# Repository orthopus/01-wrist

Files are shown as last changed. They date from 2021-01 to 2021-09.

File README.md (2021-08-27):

# Universal wrist & Tool holder

This repository contents documentation of : 

- ➡ **The Universal Wrist** : a mechanical wrist and his mechanical tool-holder. Adapted to upper-limb amputations including disarticulation of the  wrist, this mechanical wrist fits directly into a socket and connects quickly to a large number of terminal devices such as the [ORTHOPUS Work Hook or the Aesthetic Hand](https://orthopus.com/en/upper-limb-prosthetics/). *You can find [buying informations on this page](https://orthopus.com/en/universal-wrist/).*

  
  

- ➡ **The Tool holder** : compatible with the ORTHOPUS Universal Wrist. You can already find a 3D printed version, compatible with [mechanicals tools for upper limb amputees](https://github.com/orthopus/01-mechanicals-tools). *Scroll below to see the tool holder's documentation.*
  
  

>#### WARNING NOTICE BEFORE STARTING
>The Do It Yourself (DIY) versions of our solutions are not CE marked. CE marking is only applicable to solutions developed and sold by ORTHOPUS because their design follows the current regulations. ORTHOPUS cannot guarantee the “quality” of solutions replicated by third parties thanks to the documentation shared on github.

## UNIVERSAL WRIST

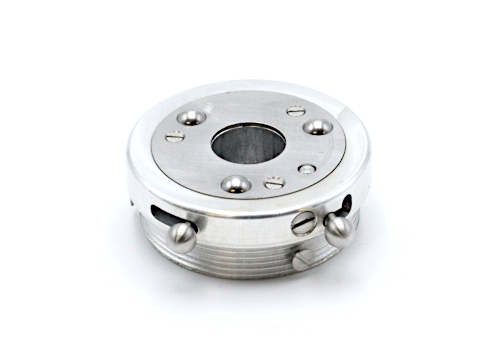
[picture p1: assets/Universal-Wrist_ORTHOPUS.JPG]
UniversalWrist_ORTHOPUS


#### HOW TO MAKE YOUR OWN UNIVERSAL WRIST

***D.I.Y difficulty level :* ⭐⭐⭐⭐⭐**

To make your own Universal Wrist, you will need advanced workshop machinery and some basics components. You can find a detailed list of equipment and the steps to follow in the **[UNIVERSAL WRIST MAKING MANUAL](./docs/wrist/UniversalWrist_making-manual.md)**)

The Bill of Material shown below is downloadable with clickable links [here](https://github.com/orthopus/01-wrist/blob/main/src/Wrist/ILL-0109-BoMGitHub.pdf) details standard components as well as parts that need to be machined.

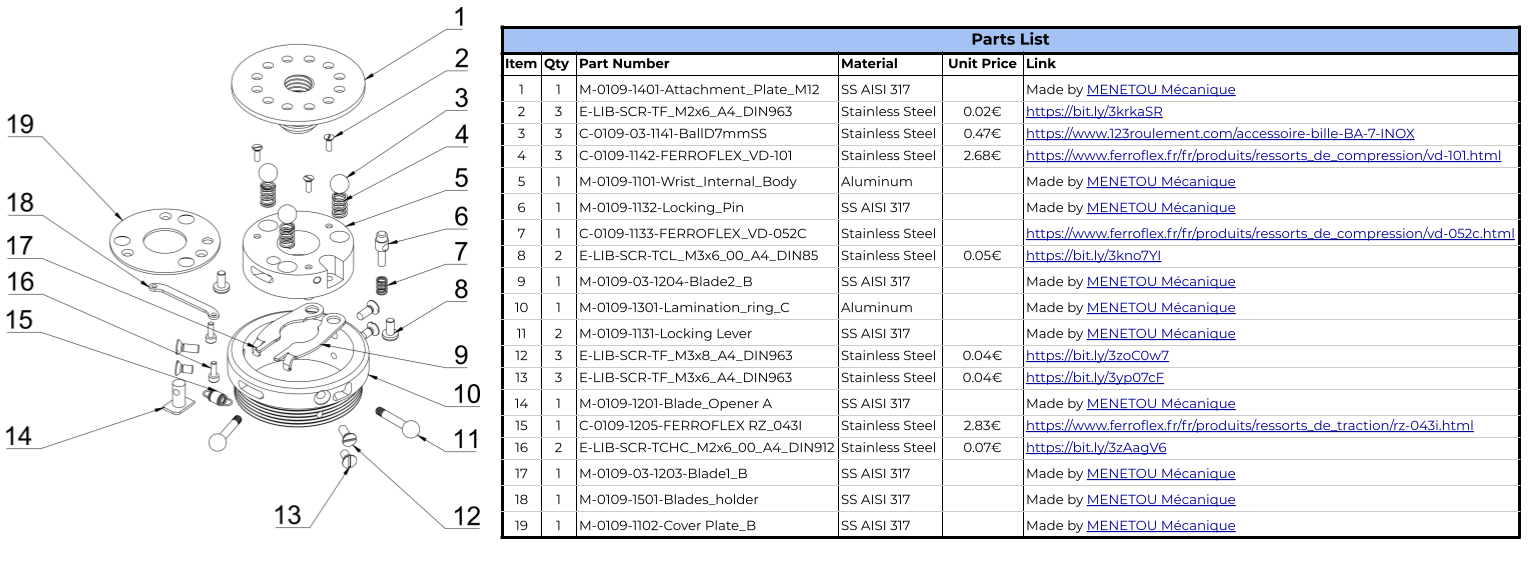
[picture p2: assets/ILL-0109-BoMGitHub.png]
ILL-0109-BomGithub


To get the best experiences with the **Universal Wrist**, full product details are provided in the [INSTRUCTIONS FOR USE](https://orthopus.com/wp-content/uploads/2021/06/IFU-OR-0109-Universal-Wrist-ORTHOPUS-Instructions-For-Use.pdf).

## TOOL HOLDER 3D PRINTED

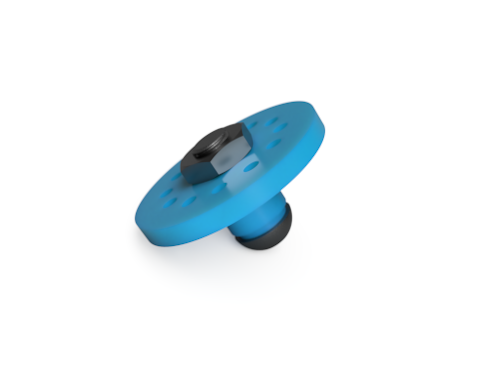
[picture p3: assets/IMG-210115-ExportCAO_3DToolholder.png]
IMG-210115-ExportCAO_3DToolholder


#### HOW TO MAKE YOUR OWN  TOOL HOLDER 3D PRINTED

***D.I.Y difficulty level :* ⭐⭐**

To make your own Tool Holder, you will need a 3D printer, a grinder machine or a metal file, and some basics screws. You can find a detailed list of equipment and the steps to follow in the **[TOOL HOLDER 3D PRINTED MAKING MANUAL](./docs/tool-holder-3D-printer/ToolHolder_3D_making-manual.md)**

You can make the Tool holder for less than 1€ : more details in the Bill of Material shown below and available with clickable links [here](https://github.com/orthopus/01-wrist/blob/main/src/Tool-holder%203D%20print/ILL-0109-DIYAttachementPlateBoM.pdf).

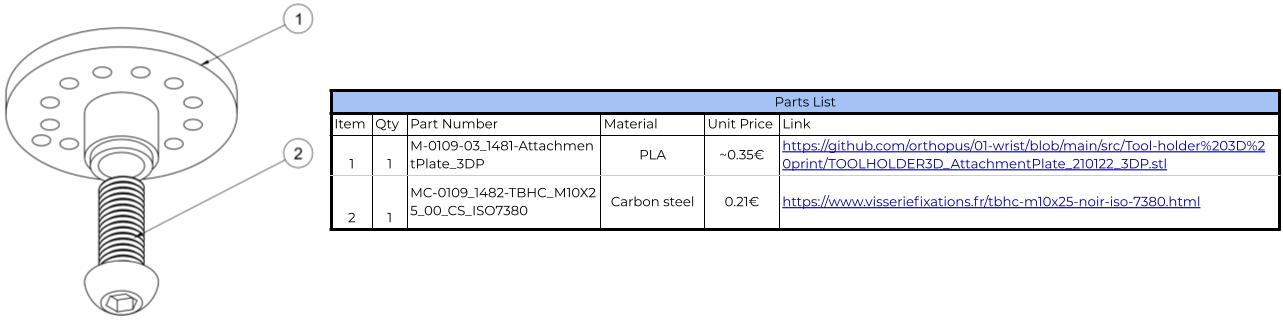
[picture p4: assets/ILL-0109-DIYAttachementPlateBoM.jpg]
ILL-0109-DIYAttachementPlateBoM


## CONTRIBUTION

Your contribution to these projects is welcome!

* You have discovered a bug or you have an improvement ideas ?
  
  * Go to the GitHub [issues](https://github.com/orthopus/01-wrist/issues) of the project.
  
* You have some time to spare, some Maker skills and you want to help us ?

  * If you need to make some design modifications, our Fusion 360 source files are available on request, don’t hesitate to ask us!

  * Read the [CONTRIBUTING](CONTRIBUTING.md) file to help us to upgrade this project

  * Read the [CODEOFCONDUCT](CODEOFCONDUCT.md) file to know community standards

## CONTACT

If you wish to contact us, you can send a message to contact@orthopus.com

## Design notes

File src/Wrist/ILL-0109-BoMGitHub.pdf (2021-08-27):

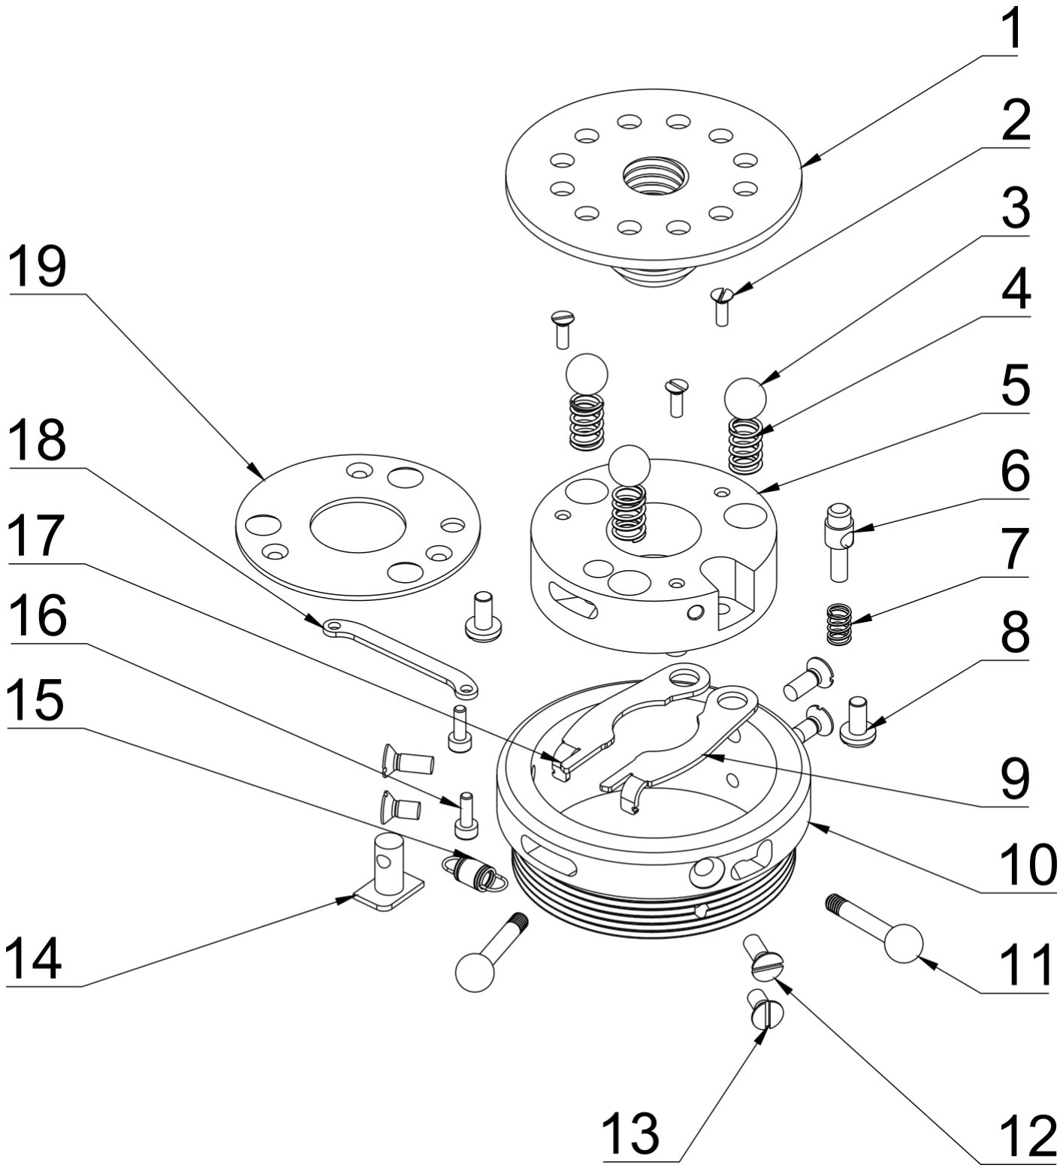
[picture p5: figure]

### Parts List

Item | Qty | Part Number | Material | Unit Price | Link
1 | 1 | M-0109-1401-Attachment_Plate_M12 | SS AISI 317 | | Made by MENETOU Mécanique (https://www.menetoumecanique.com/)
2 | 3 | E-LIB-SCR-TF_M2x6_A4_DIN963 | Stainless Steel | 0.02€ | https://bit.ly/3krkaSR
3 | 3 | C-0109-03-1141-BallD7mmSS | Stainless Steel | 0.47€ | https://www.123roulement.com/accessoire-bille-BA-7-INOX
4 | 3 | C-0109-1142-FERROFLEX_VD-101 | Stainless Steel | 2.68€ | https://www.ferroflex.fr/fr/produits/ressorts_de_compression/vd-101.html
5 | 1 | M-0109-1101-Wrist_Internal_Body | Aluminum | | Made by MENETOU Mécanique (https://www.menetoumecanique.com/)
6 | 1 | M-0109-1132-Locking_Pin | SS AISI 317 | | Made by MENETOU Mécanique (https://www.menetoumecanique.com/)
7 | 1 | C-0109-1133-FERROFLEX_VD-052C | Stainless Steel | | https://www.ferroflex.fr/fr/produits/ressorts_de_compression/vd-052c.html
8 | 2 | E-LIB-SCR-TCL_M3x6_00_A4_DIN85 | Stainless Steel | 0.05€ | https://bit.ly/3kno7YI (https://www.visseriefixations.fr/vis-a-metaux/tete-cylindrique/tete-cylindrique-large-fendue-tcl-din-85/inox-a4/tcl-m3x6-inox-a4-din-85.html)
9 | 1 | M-0109-03-1204-Blade2_B | SS AISI 317 | | Made by MENETOU Mécanique (https://www.menetoumecanique.com/)
10 | 1 | M-0109-1301-Lamination_ring_C | Aluminum | | Made by MENETOU Mécanique (https://www.menetoumecanique.com/)
11 | 2 | M-0109-1131-Locking Lever | SS AISI 317 | | Made by MENETOU Mécanique (https://www.menetoumecanique.com/)
12 | 3 | E-LIB-SCR-TF_M3x8_A4_DIN963 | Stainless Steel | 0.04€ | https://bit.ly/3zoC0w7
13 | 3 | E-LIB-SCR-TF_M3x6_A4_DIN963 | Stainless Steel | 0.04€ | https://bit.ly/3yp07cF
14 | 1 | M-0109-1201-Blade_Opener A | SS AISI 317 | | Made by MENETOU Mécanique (https://www.menetoumecanique.com/)
15 | 1 | C-0109-1205-FERROFLEX RZ_043I | Stainless Steel | 2.83€ | https://www.ferroflex.fr/fr/produits/ressorts_de_traction/rz-043i.html
16 | 2 | E-LIB-SCR-TCHC_M2x6_00_A4_DIN912 | Stainless Steel | 0.07€ | https://bit.ly/3zAagV6
17 | 1 | M-0109-03-1203-Blade1_B | SS AISI 317 | | Made by MENETOU Mécanique (https://www.menetoumecanique.com/)
18 | 1 | M-0109-1501-Blades_holder | SS AISI 317 | | Made by MENETOU Mécanique (https://www.menetoumecanique.com/)
19 | 1 | M-0109-1102-Cover Plate_B | SS AISI 317 | | Made by MENETOU Mécanique (https://www.menetoumecanique.com/)

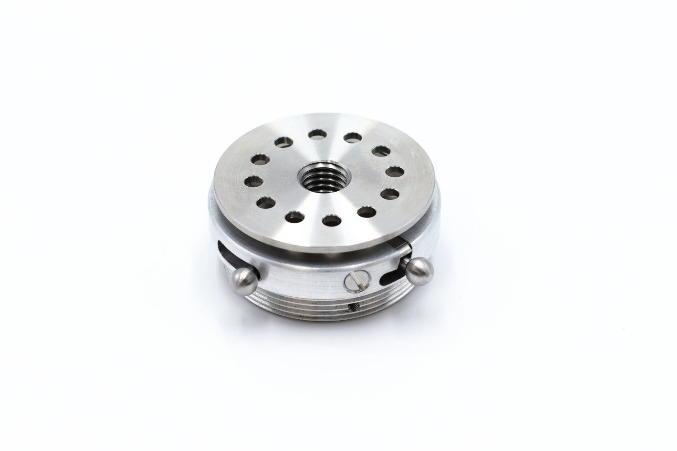
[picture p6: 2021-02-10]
assets/UniversalWrist_ORTHOPUS.JPG

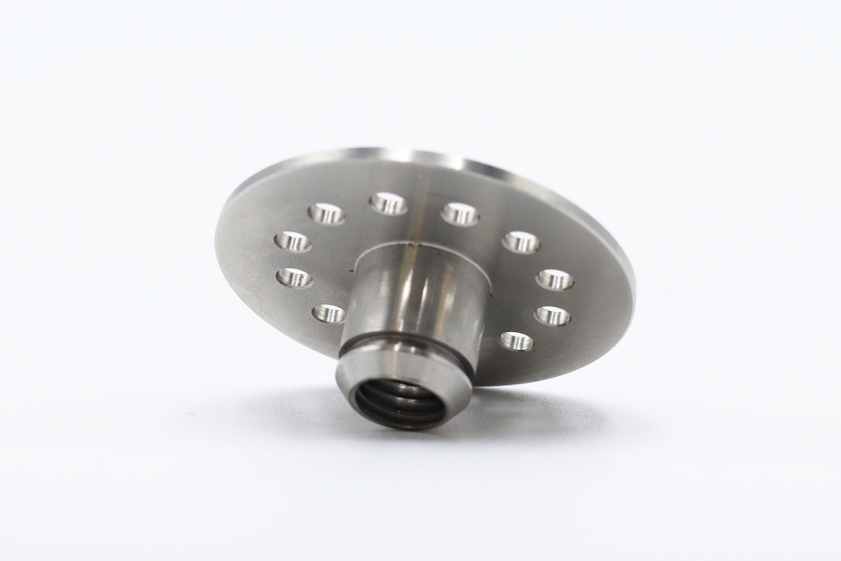
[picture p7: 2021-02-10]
assets/Toolholder_machined_ORTHOPUS.JPG

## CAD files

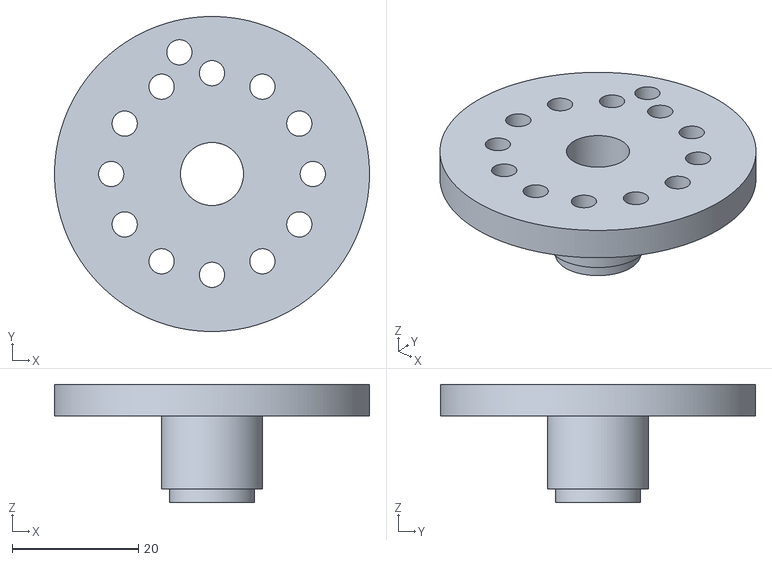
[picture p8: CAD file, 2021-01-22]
src/Tool-holder 3D print/TOOLHOLDER3D_AttachmentPlate_210122_3DP.stl
50.0 x 50.0 x 18.8

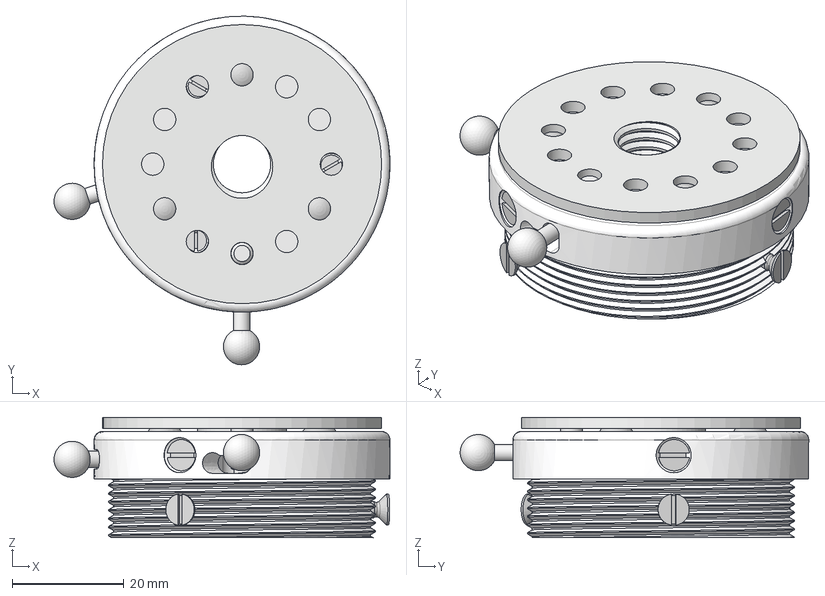
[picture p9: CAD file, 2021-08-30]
src/Wrist/PRD-0109-1xxx_C-Wrist_v1.4.4.step
60.2 x 62.4 x 21.5 mm
M-0109_1301-Lamination_ring_C
M-0109-1401-Attachment_Plate_M12_A
M-0109_1101-Wrist_Internal_Body_C
M-0109_1132-Locking_Pin_A
M-0109_1131-Locking_Lever_B
C-0109_1133-FERROFLEX_VD-052C
M-0109_1102-Cover Plate_B
C-0109-1141-Ball_D7_mm_SS x 3
C-0109_1142-FERROFLEX_VD-101 x 3
210208-2X6 x 3
M-0109_1202-Blade_Opener_Lever_B
M-0109-03_1203-Blade1_B
C-0109_1205-FERROFLEX RZ_043I
_M-0109_1201-Blade_Opener A
M-0109-03_1204-Blade2_B
E-LIB-SCR-TCL_M2x6_00_A4_DIN85 x 2
M-0109-1501-Blades_holder
E-LIB-SCR-TCHC_M2x6_00_A4_DIN912 x 2

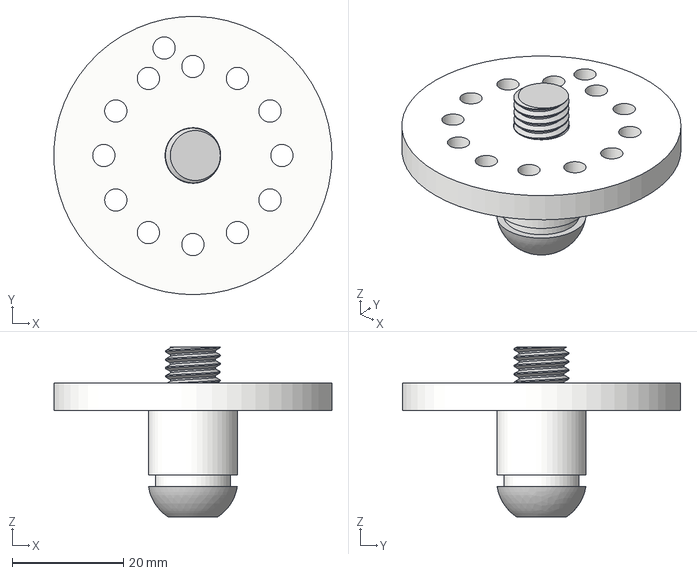
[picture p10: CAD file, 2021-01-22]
src/Tool-holder 3D print/TOOLHOLDER3D_DIY-Attachment-Plate_210122.step
50.0 x 50.0 x 30.5 mm
M-0109-03_1481-AttachmentPlate_3DP
MC-0109_1482-TBHC_M10X25_00_CS_ISO7380

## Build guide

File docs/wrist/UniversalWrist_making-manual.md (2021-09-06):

# Universal Wrist : Making Manual

UniversalWrist_ORTHOPUS

In this manual you will find information to help you understand in details how is made the ORTHOPUS Universal Wrist so you can make it yourself (modern machine shop workstations required), directly with a manufacturer or simply repair/upgrade it yourself.

### **List of parts**

On the following picture, you can find an exploded view showing all the parts of the Universal Wrist. In the table, links allow you to find where components can be purchased or, for the machined ones, where we are manufacturing them. You can download the ***Bill of Material stored [here](https://github.com/orthopus/01-wrist/blob/main/src/Wrist/ILL-0109-BoMGitHub.pdf) to get clickable links.***

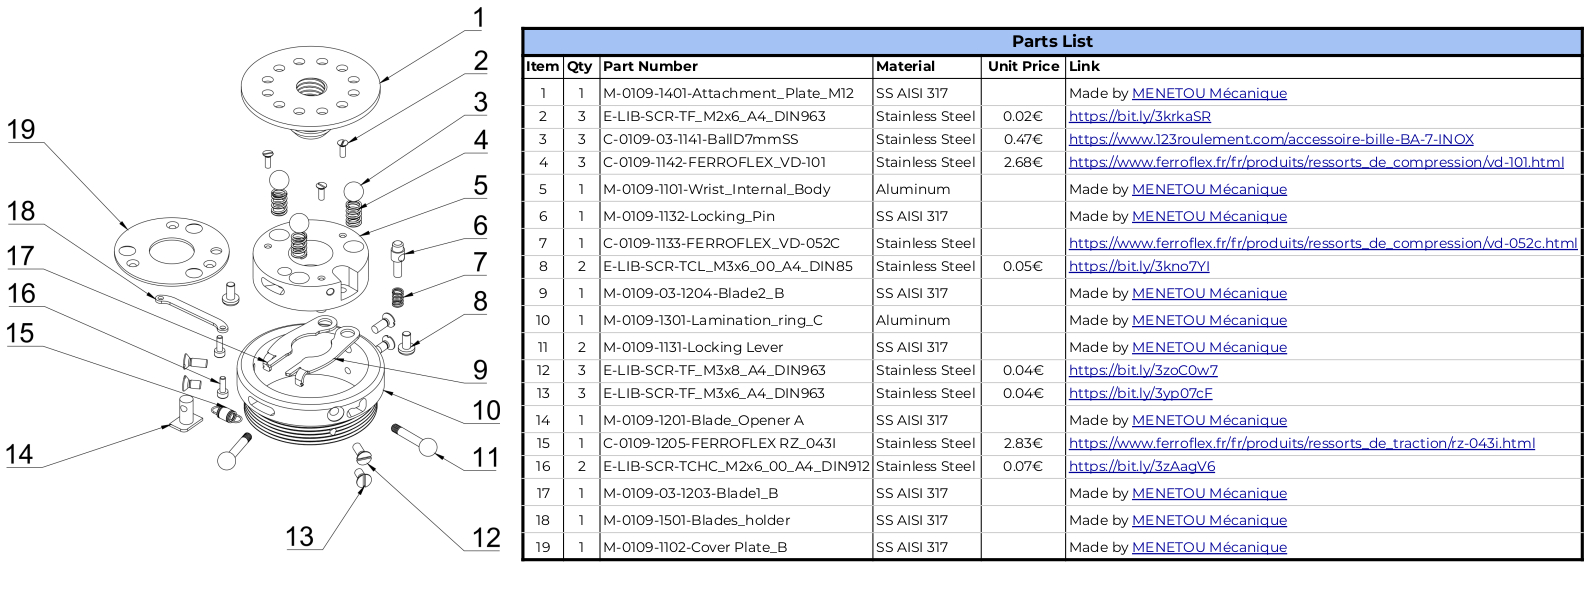
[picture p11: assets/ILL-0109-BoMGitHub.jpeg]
ILL-0109-BomGithub


### **Manufacturing**

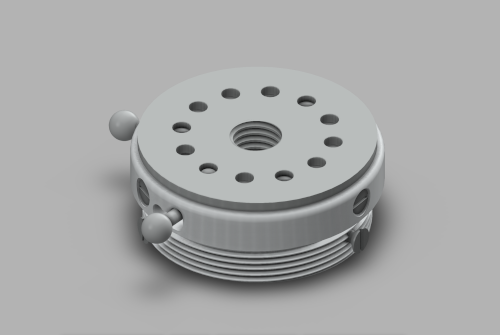
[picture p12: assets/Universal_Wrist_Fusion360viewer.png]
Universal_Wrist_Fusion360viewer (https://orthopus8.autodesk360.com/g/shares/SH919a0QTf3c32634dcf53115fb3b05c0f27)


🧐 *Tip : open the image in a new tab to view the Tennis Ball Holder in Fusion 360 viewer*

Manufacturing the Universal Wrist requires advanced knowledge and machinery such as lathe, milling and drilling machines, etc... However, if you have all the required machinery, with the .STEP files [available here](https://github.com/orthopus/01-wrist/blob/main/src/Wrist/PRD-0109-1xxx_C-Wrist_v1.4.4.step) and the drawings [available here](https://github.com/orthopus/01-wrist/blob/main/src/Wrist/DRW-0109-1xxx-Wrist_Drawing_C.pdf) of the Universal Wrist, you should be able to make your own.

ORTHOPUS has chosen [Menetou Mécanique](https://www.menetoumecanique.com/) to manufacture in France 100% of its Universal Wrist.

### **Assembly**

**List of required equipment**

- A 0.5 flat screwdriver
- A 0.8 flat screwdriver
- A 1.5 hex key
- Threadlocking adhesive 

**Instructions**

With the picture below, you should be able to fully assemble or disassemble the Universal Wrist. To screw the M2 screws of the retaining bar (step 6), please use 1.5 hex key. For the 3 countersunk M2 screws holding the cover plate, please use a 0.5 flat screwdriver and for the M3 ones (step 13) a 0.8 flat screwdriver. Please use threadlocking adhesive to lock the screws when you are screwing them (steps 2, 6, 11, 13, 14, 15).

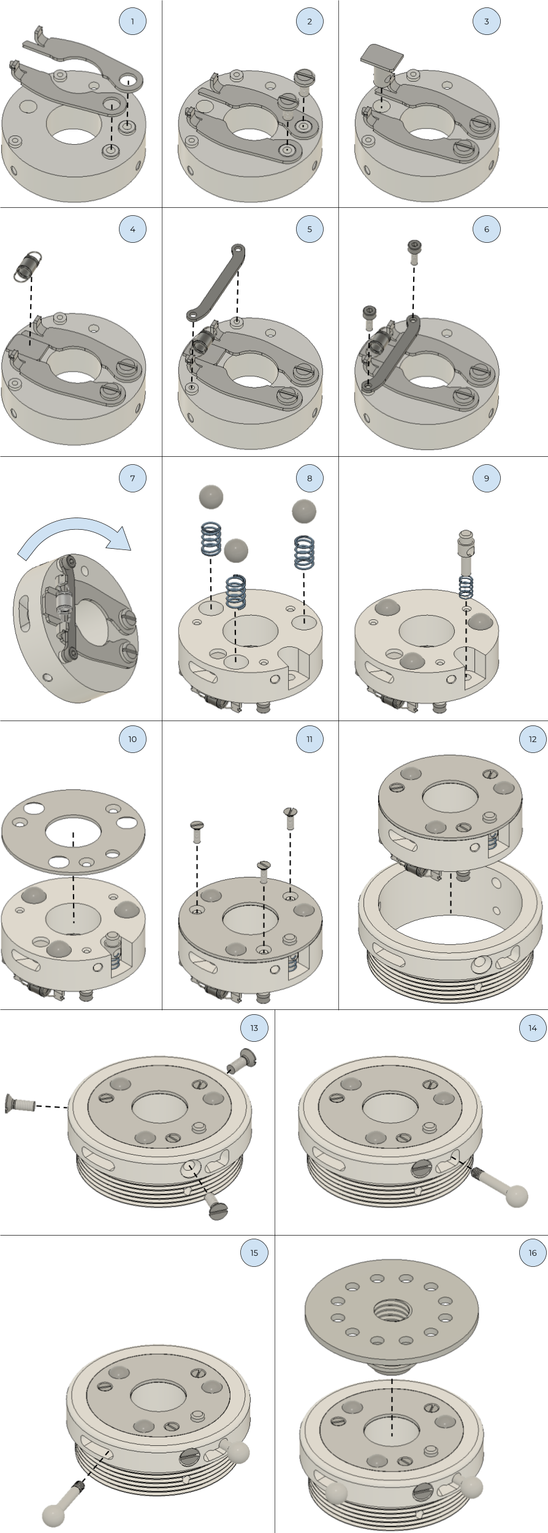
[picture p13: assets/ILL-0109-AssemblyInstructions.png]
ILL-0109-AssemblyInstructions


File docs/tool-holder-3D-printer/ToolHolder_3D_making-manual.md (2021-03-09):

# Tool holder 3D printer : Making Manual

IMG-210115-ExportCAO_3DToolholder

In this manual, you will find all the resources to design the Tool Holder 3D printer. 

:warning:  ***Warning*** :warning: 

For each tool, such as [the pick or tennis ball holders](https://github.com/orthopus/01-mechanicals-tools), a tool holder is required. This assembly manual only details how to make a tool holder which will be required to connect a tool to the universal wrist. 

### **List of Equipment**

**To design the Tool Holder you will need :**

- A 3D Printer
- PLA type filament
- A screw (TBHC M10 x 25 mm, Stainless Steel A2, ISO 7380)
- A bolt (Hm M10, zinc plated, DIN439)

**Tools :** 

- A grinding machine or a metal file 
- Drill or screwdriver and drill bits
- An Allen key (size 6)

You can download ***the Bill of Material stored [here](https://github.com/orthopus/01-wrist/blob/main/src/Tool-holder%203D%20print/ILL-0109-DIYAttachementPlateBoM.pdf) to get clickable links***.

ILL-0109-DIYAttachementPlateBoM

### **The 3D Printed Body**

The base body of the **Tool Holder** will house the screw that will allow the Tool Holder to clip on the Wrist. It will also allow the indexed rotation of the tool in the wrist thanks to the 12 small holes arranged in a circle.

The .STL file of the 3D printed body is available here.

We used the Ultimaker Cura slicer and an Ultimaker Extended 2+ 3D printer.

Following parameter were used:

- Layer height: 0.15 mm

- Infill density: 50%

- Print speed: 50 mm/s

- Fan speed: 100%

- Build plate adhesion type: Brim

### **Machining Process**

The screw does not have the right head outer diameter to go through the universal wrist inner bore. You will have to reduce this diameter by grinding the head or file it. The goal is to reach an external head diameter smaller than 16 mm. 

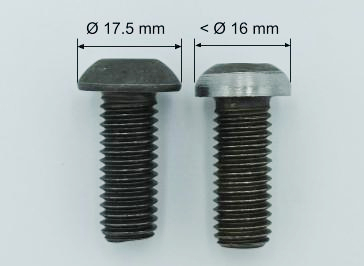
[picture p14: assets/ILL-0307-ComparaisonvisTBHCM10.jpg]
ILL-0307-ComparaisonvisTBHCM10


### **Assembly** 

To assemble the Tool Holder 3D Printed, simply insert the modified M10 screw into the 3D printed body. Accordingly to which tool you will be connecting to the Tool Holder 3D Printed, further assembly instructions will be provided.

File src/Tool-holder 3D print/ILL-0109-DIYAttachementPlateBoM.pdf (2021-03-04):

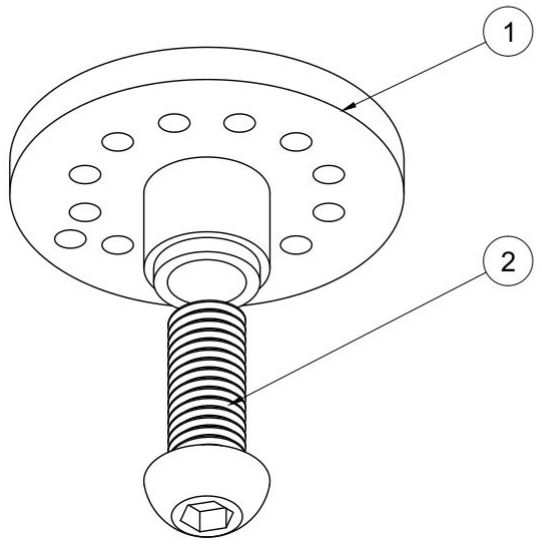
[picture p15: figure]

Parts List
Item | Qty | Part Number | Material | Unit Price | Link
1 | 1 | M-0109-03_1481-Attachmen tPlate_3DP | PLA | ~0.35€ | https://github.com/orthopus/01-wrist/blob/main/src/Tool-holder%203D%2
0print/TOOLHOLDER3D_AttachmentPlate_210122_3DP.stl (https://github.com/orthopus/01-wrist/blob/main/src/Tool-holder%203D%20print/TOOLHOLDER3D_AttachmentPlate_210122_3DP.stl)

2 1

MC-0109_1482-TBHC_M10X2
5_00_CS_ISO7380 | Carbon steel | 0.21€ | https://www.visseriefixations.fr/tbhc-m10x25-noir-iso-7380.html

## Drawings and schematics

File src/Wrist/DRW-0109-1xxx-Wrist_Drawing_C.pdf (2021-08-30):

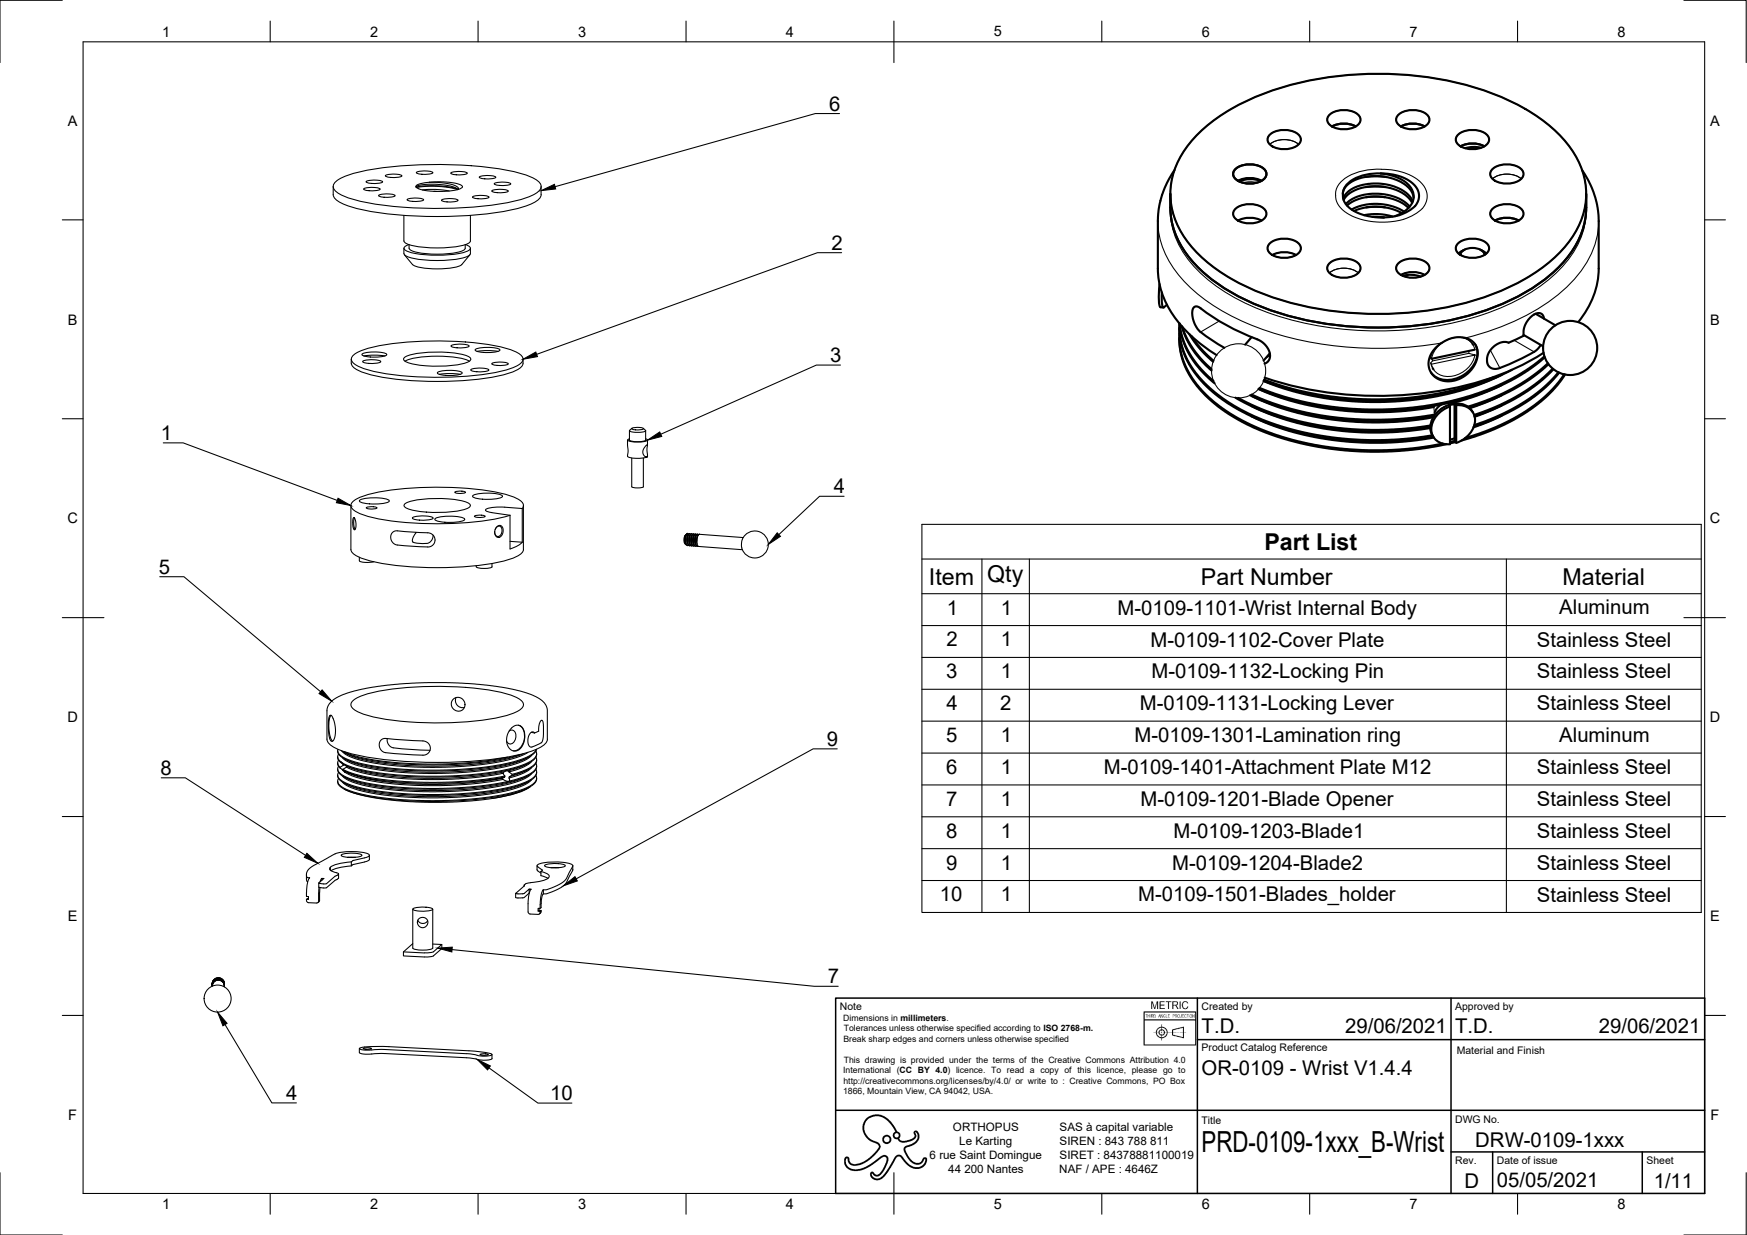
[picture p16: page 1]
Part List

Item | Qty | Part Number | Material
1 | 1 | M-0109-1101-Wrist Internal Body | Aluminum
2 | 1 | M-0109-1102-Cover Plate | Stainless Steel
3 | 1 | M-0109-1132-Locking Pin | Stainless Steel
4 | 2 | M-0109-1131-Locking Lever | Stainless Steel
5 | 1 | M-0109-1301-Lamination ring | Aluminum
6 | 1 | M-0109-1401-Attachment Plate M12 | Stainless Steel
7 | 1 | M-0109-1201-Blade Opener | Stainless Steel
8 | 1 | M-0109-1203-Blade1 | Stainless Steel
9 | 1 | M-0109-1204-Blade2 | Stainless Steel
10 | 1 | M-0109-1501-Blades_holder | Stainless Steel

Note Dimensions in millimeters. Tolerances unless otherwise specified according to ISO 2768-m. Break sharp edges and corners unless otherwise specified This drawing is provided under the terms of the Creative Commons Attribution 4.0 International (CC BY 4.0) licence. To read a copy of this licence, please go to http://creativecommons.org/licenses/by/4.0/ or write to : Creative Commons, PO Box 1866, Mountain View, CA 94042, USA. | Created by T.D. 29/06/2021 | Approved by T.D. 29/06/2021

Product Catalog Reference OR-0109 - Wrist V1.4.4 | Material and Finish

ORTHOPUS SAS à capital variable Le Karting SIREN : 843 788 811 6 rue Saint Domingue SIRET : 84378881100019 44 200 Nantes NAF / APE : 4646Z | Title PRD-0109-1xxx_B-Wrist | DWG No. DRW-0109-1xxx

Rev. D | Date of issue 05/05/2021 | Sheet

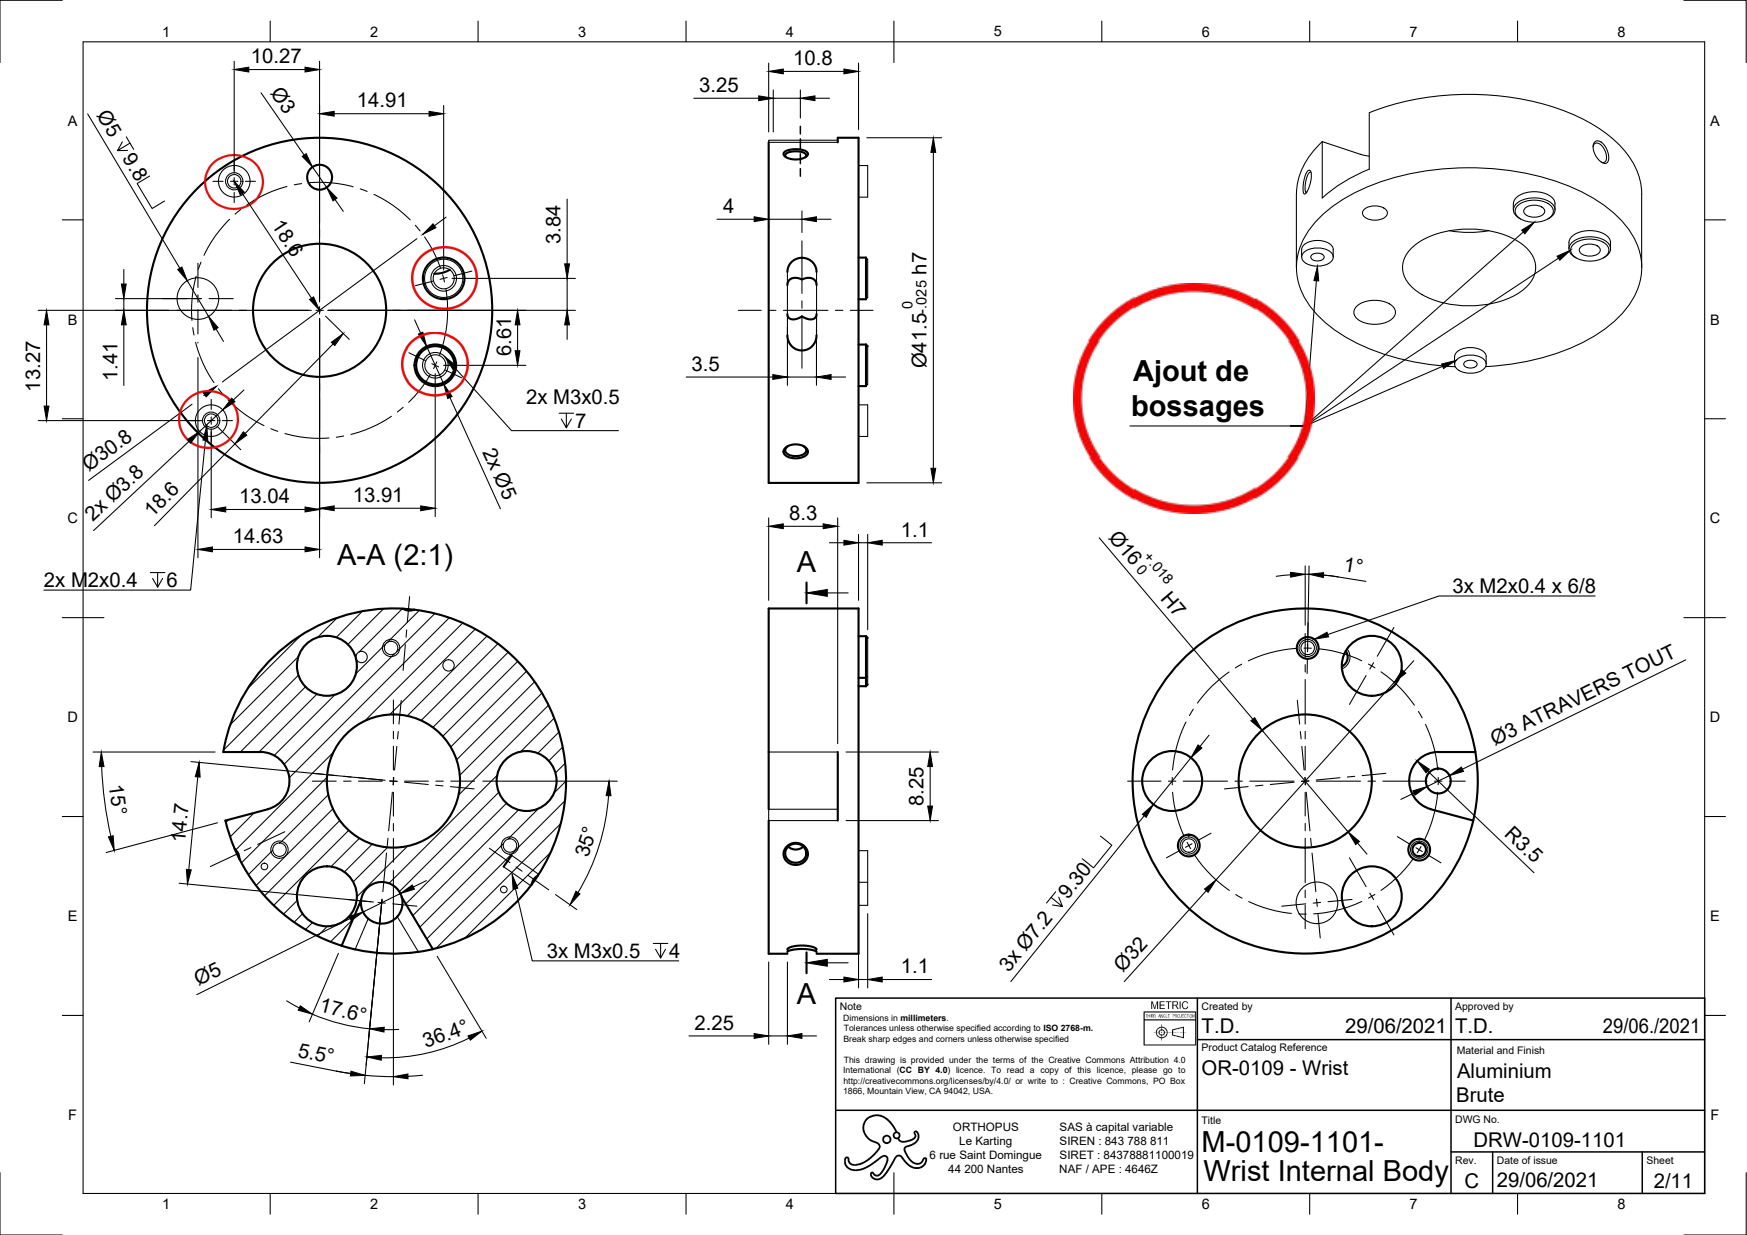
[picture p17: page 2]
Ø3 ATRAVERS TOUT; Ajout de

Wrist Internal Body Ø41.5 0-.025 h7

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

Product Catalog Reference OR-0109 - Wrist | Material and Finish Aluminium Brute

ORTHOPUS SAS à capital variable SIREN : 843 788 811 NAF / APE : 4646Z | Title M-0109-1101- | DWG No. DRW-0109-1101

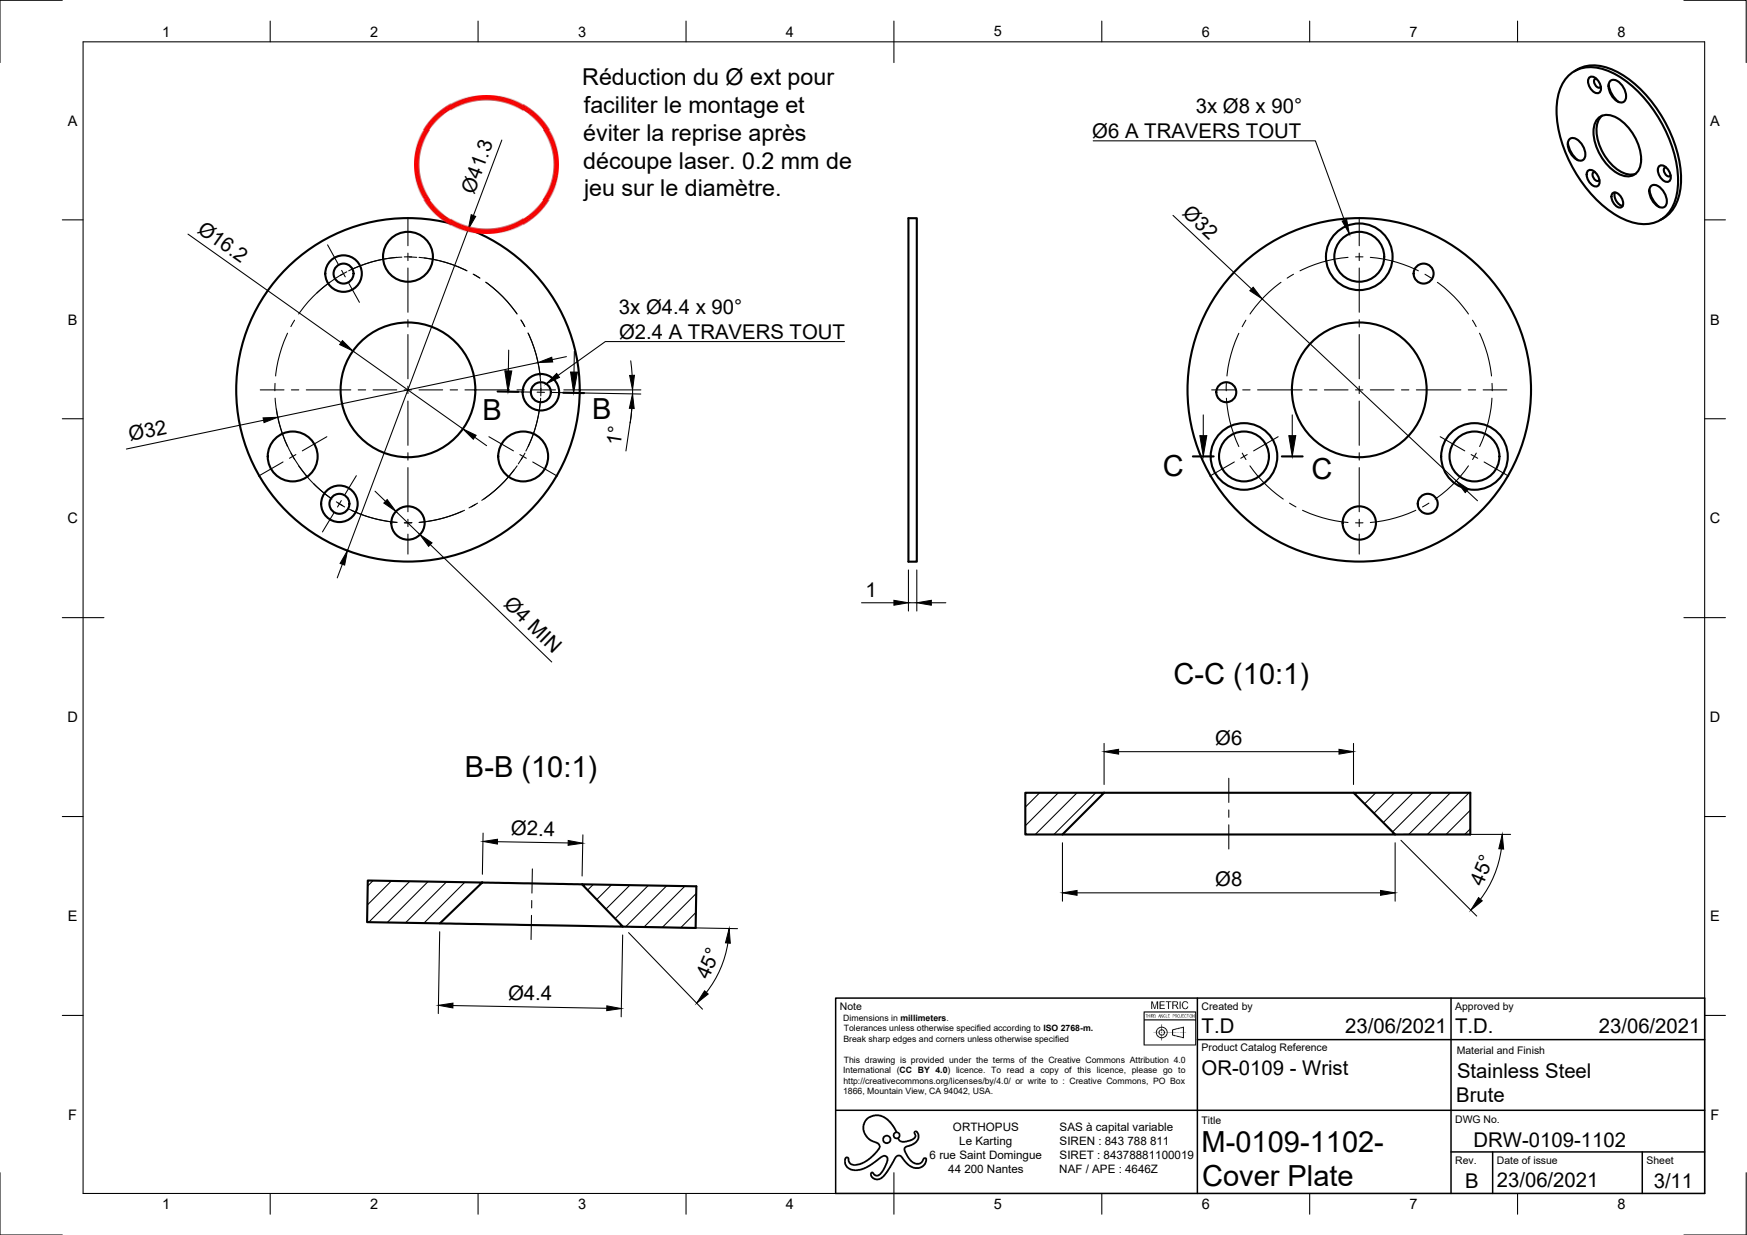
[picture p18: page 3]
3x Ø4.4 x 90° Ø2.4 A TRAVERS TOUT; Ø4 MIN; 3x Ø8 x 90° Ø6 A TRAVERS TOUT

Réduction du Ø ext pour
faciliter le montage et
éviter la reprise après
découpe laser. 0.2 mm de
jeu sur le diamètre.

Note Dimensions in millimeters. Tolerances unless otherwise specified according to ISO 2768-m. Break sharp edges and corners unless otherwise specified This drawing is provided under the terms of the Creative Commons Attribution 4.0 International (CC BY 4.0) licence. To read a copy of this licence, please go to http://creativecommons.org/licenses/by/4.0/ or write to : Creative Commons, PO Box 1866, Mountain View, CA 94042, USA. | Created by T.D 23/06/2021 | Approved by T.D. 23/06/2021

Product Catalog Reference OR-0109 - Wrist | Material and Finish Stainless Steel Brute

ORTHOPUS SAS à capital variable SIREN : 843 788 811 NAF / APE : 4646Z | Title M-0109-1102-Cover Plate | DWG No. DRW-0109-1102

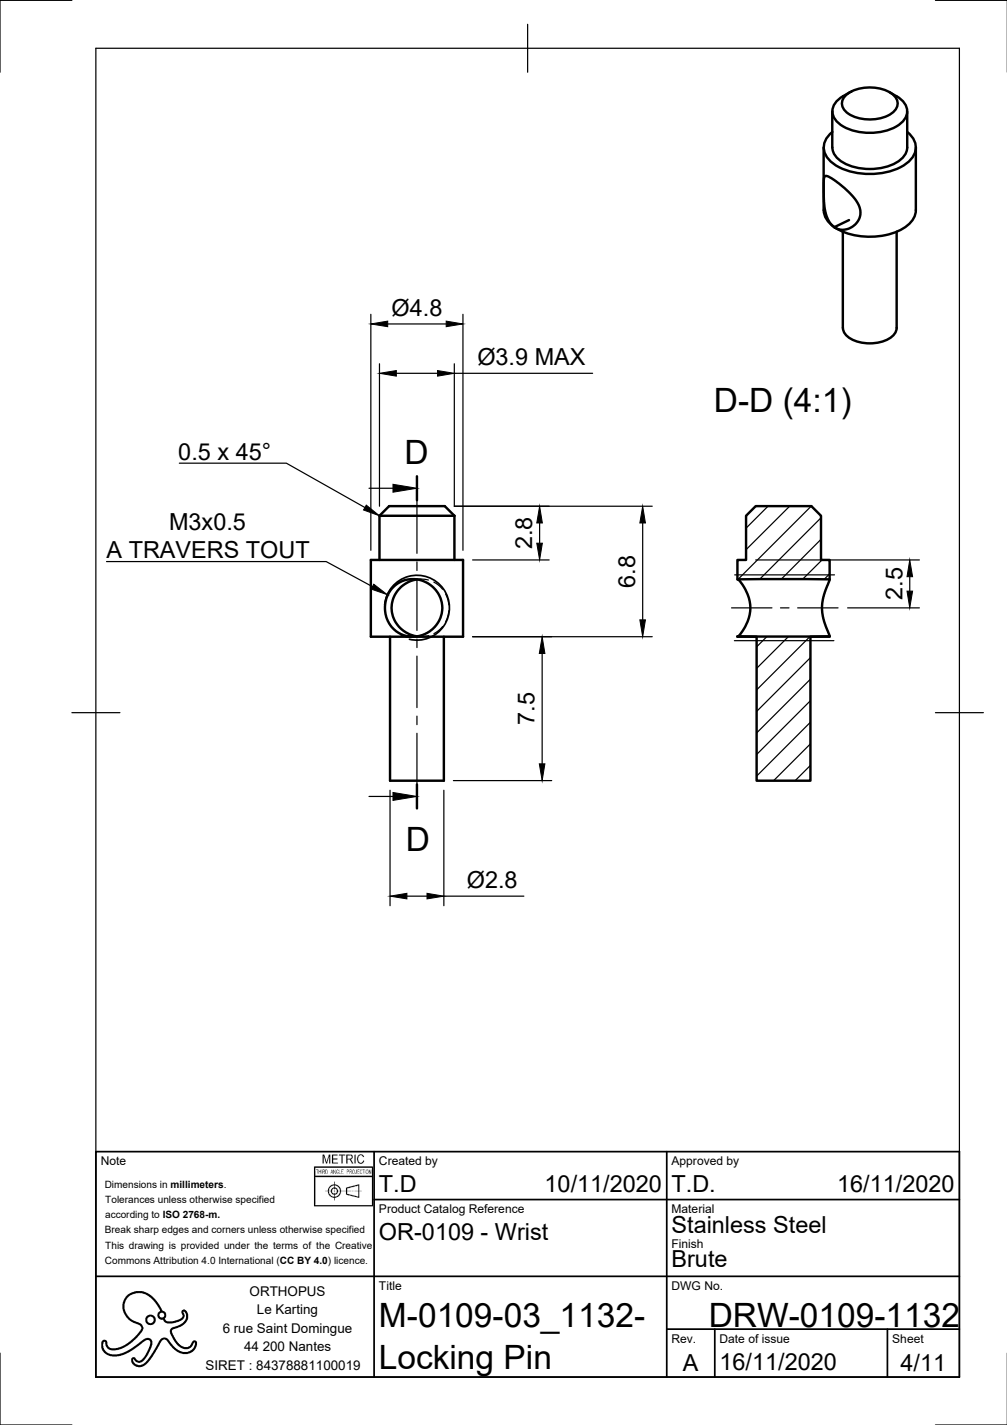
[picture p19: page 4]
A TRAVERS TOUT; Ø3.9 MAX

Note Dimensions in millimeters. Tolerances unless otherwise specified according to ISO 2768-m. Break sharp edges and corners unless otherwise specified This drawing is provided under the terms of the Creative Commons Attribution 4.0 International (CC BY 4.0) licence. | Created by T.D 10/11/2020 | Approved by T.D. 16/11/2020

Product Catalog Reference OR-0109 - Wrist | Material Stainless Steel Finish Brute

ORTHOPUS | Title M-0109-03_1132-Locking Pin | DWG No. DRW-0109-1132

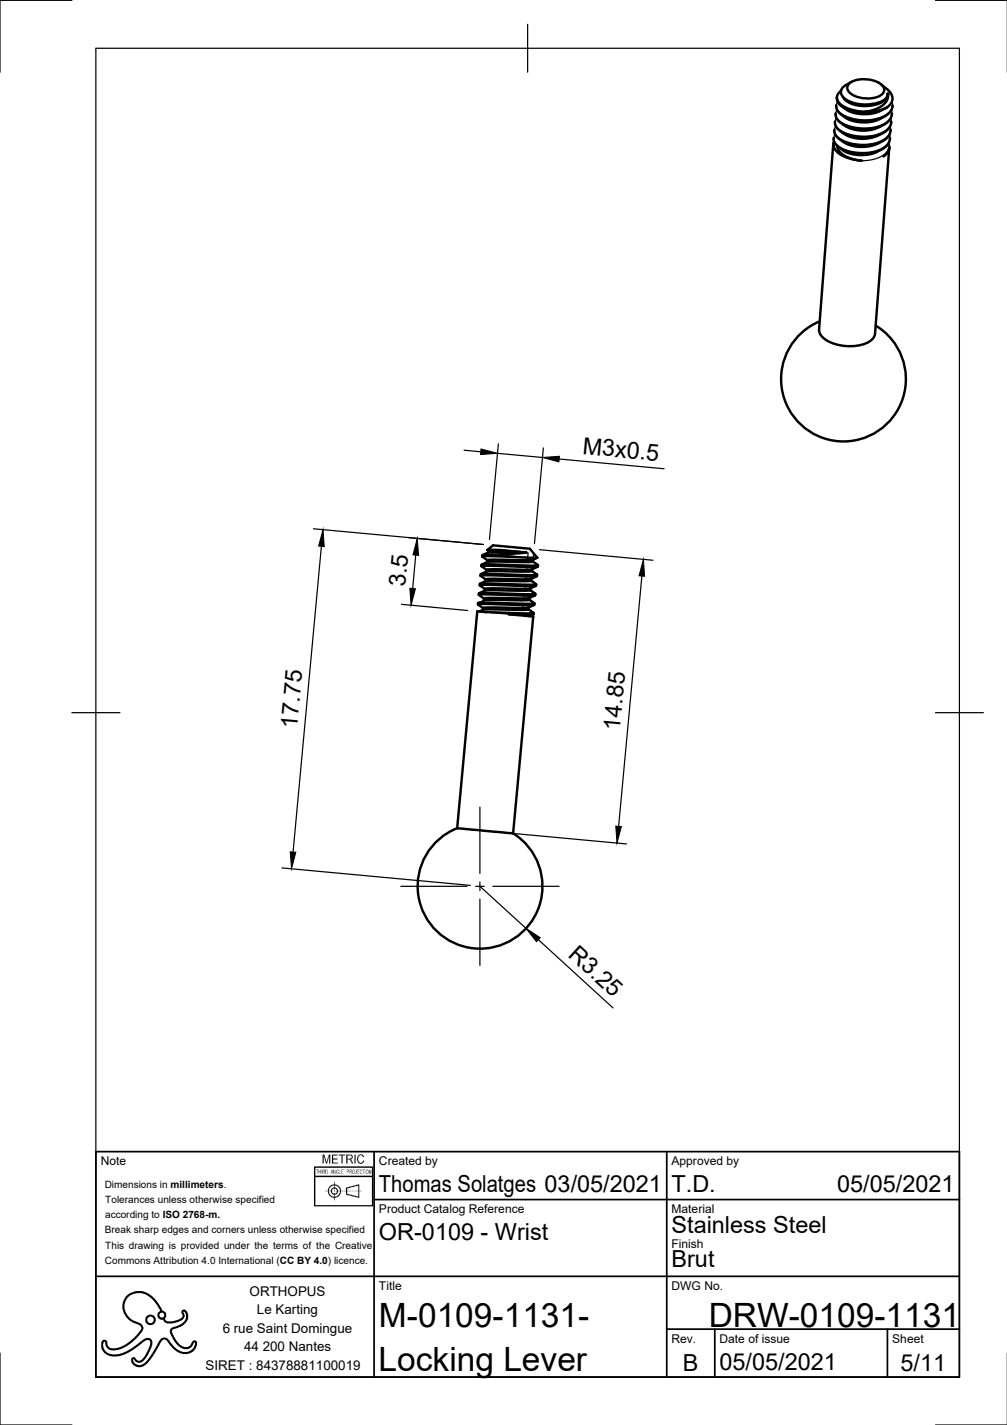
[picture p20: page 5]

Note Dimensions in millimeters. Tolerances unless otherwise specified according to ISO 2768-m. Break sharp edges and corners unless otherwise specified This drawing is provided under the terms of the Creative Commons Attribution 4.0 International (CC BY 4.0) licence. | Created by Thomas Solatges 03/05/2021 | Approved by T.D. 05/05/2021

Product Catalog Reference OR-0109 - Wrist | Material Stainless Steel Finish Brut

ORTHOPUS | Title M-0109-1131-Locking Lever | DWG No. DRW-0109-1131

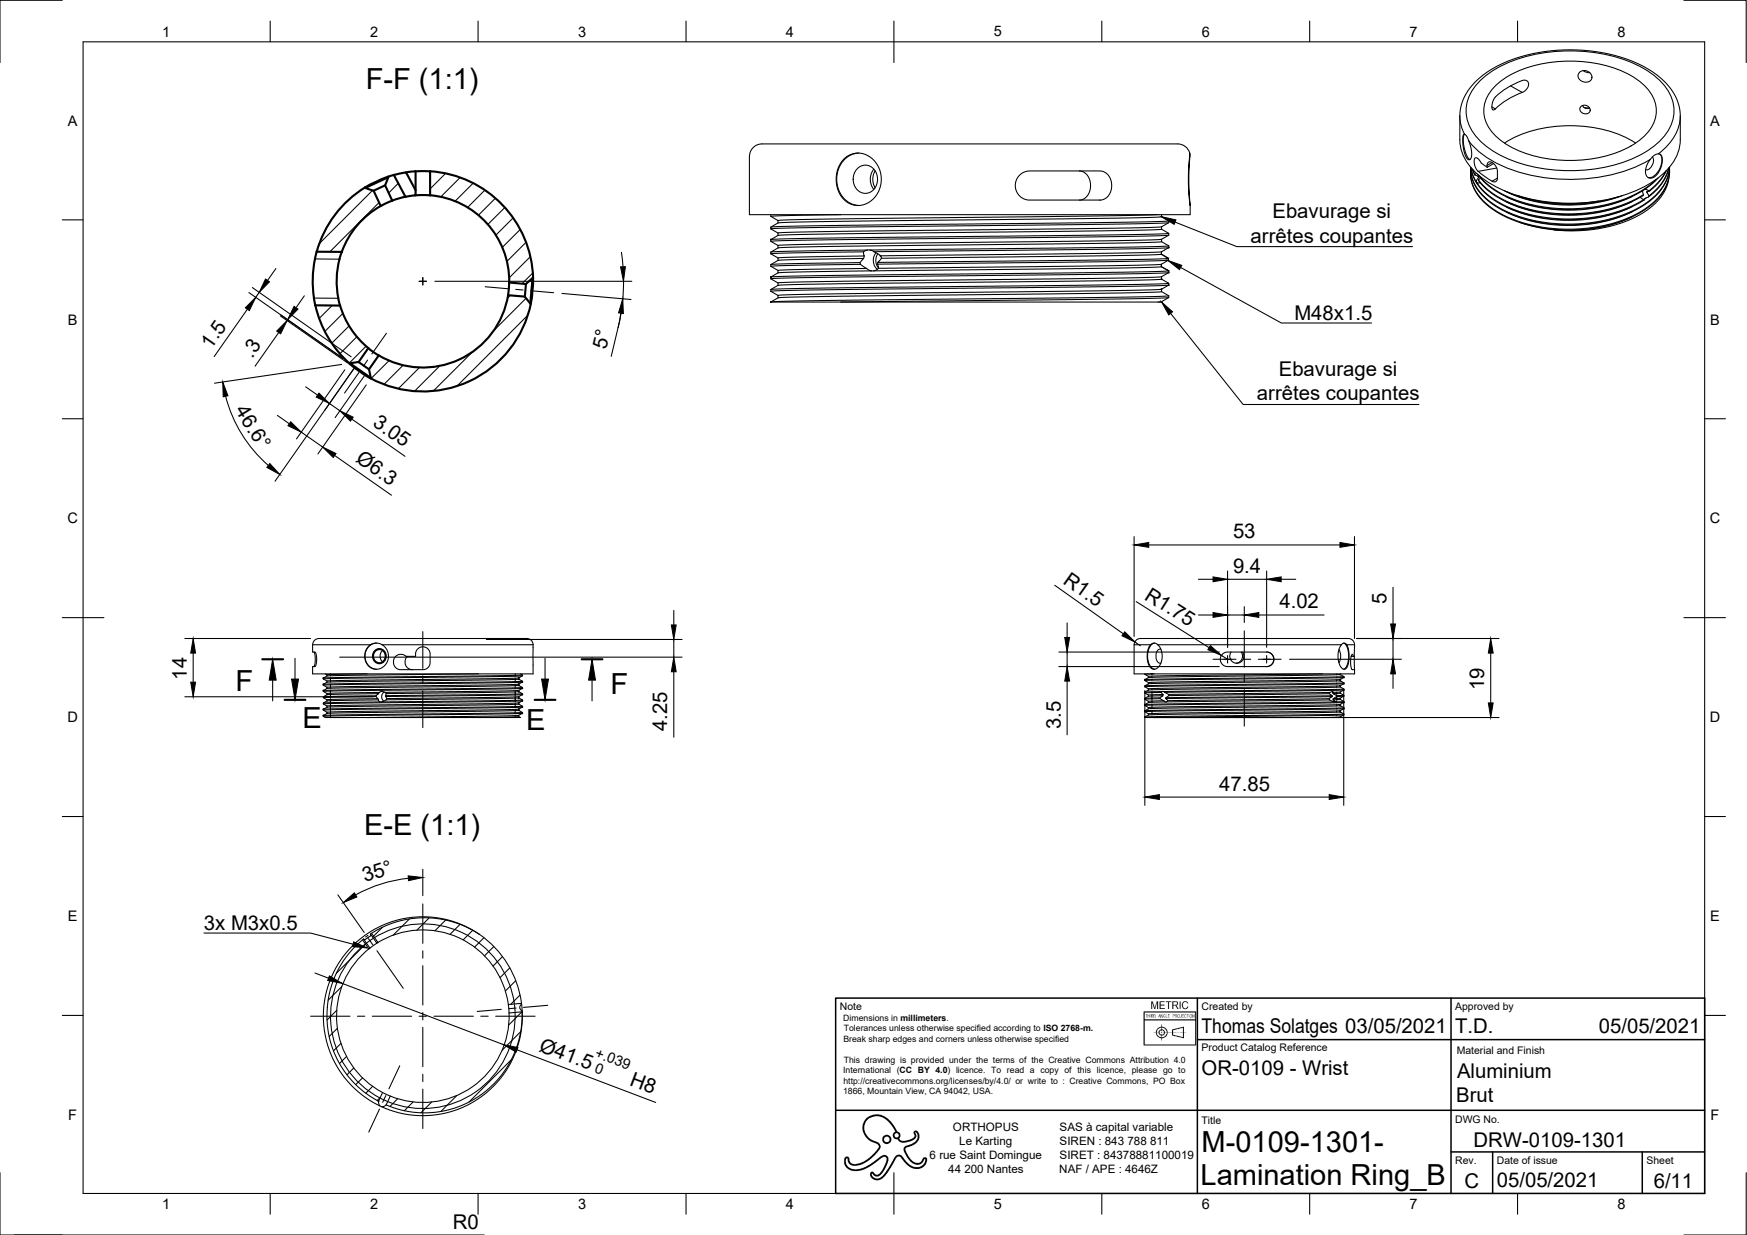
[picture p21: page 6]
Ebavurage si arrêtes coupantes
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

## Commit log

2020-12-14 Creation de l'arborescence
2021-02-25 Add files via upload
    Ajout mise en plan des pièces usinées du poignet P3
2021-03-02 Update UniversalWrist_making-manual.md
    added assembly instructions
2021-03-02 Update UniversalWrist_making-manual.md
    Updated assembly illus
